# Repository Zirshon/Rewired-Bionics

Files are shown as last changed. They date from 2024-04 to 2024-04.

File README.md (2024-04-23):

In this file, there are instructions on how to recreate each part of Rewired Bionics' Waver Fin prosthetic attachment. Of these parts, the most likely to break is the body, and it is also the simplest to remake. It is recommended to save the spine if the body breaks and reuse that. If the Waver Fin breaks, it is not suggested to remake the shell. It is still fully functional without it, though it is more fragile without. The shell can be costly to remake, and requires specialized tools. If the spine breaks somehow, it is not suggested to personally remake it, as the tools required to make it can be dangerous  without prior training. Any further inquiries can be sent to loffenbe@asu.edu, jburdorf@asu.edu, or claypete45@gmail.com.

Manufacturing Process of Attachment:

  **In order to make a new body:** 
    To make a new body, PETG filament is required. The required tools are a 3D printer capable of printing the PETG filament with a printing area of at least 7"x7"x10" (A Prusa i3 MK3 was originally used), as well as a drill with a 1/2" bit.
    To make the new body, download the file labeled "Waver Fin Body.STL" and run it through a slicer. A slicer is a program designed to make STL files readable by 3D printers, and should be included with any 3D printer. They are all different and will likely require some researching on how to use them, but the details that should be used regardless are as follows: Use **100% infill**. This will prevent any water from being trapped in the body and molding. Print the Waver Fin **vertically**, such that the spine hole runs directly up and down. This is not technically required, but it will make the whole thing easier to clean up, and ensure it can survive the same forces it was tested for. Any sort of support material is fine, and should not affect the final stability of the Waver Fin, though tree support was what was used originally, and is generally fairly painless. Those are the only major settings to use, and it should be ready to print. The printing itself will take several hours. **Be sure to follow the temperature and printing instructions on the PETG filament**. 
    After it is done printing, remove the support material from it. This is usually as simple as snapping it off, though sometimes a decent amount of force is needed. Feel free to use pliers or any other sort of tools to speed it along. You may also want to use some sandpaper to get rid of risidual sharp edges from the supports. After you are satisfied, use the drill and bit to excavate the spine cavity of the body. 3D printers are never completely accurate, so this will likely be necessary. Make sure to keep the drill level while doing this, and stay on the path.
    The final step is now to put the spine back in the body. To do this, unscrew the adaptor. Place the body in a vice grip, tightening on the crossbar of the Waver Fin. Using a rubber mallet, gently hammer the spine down into the cavity until the top of the screw is level with the top of the body. Place a 2" washer with a 1/2" bore on the end of the fin, then rescrew an adaptor back on, torquing it into place.
    
  **In order to make a new shell:**
    To make a new shell, two sheets of kydex large enough to cover the body, as well as a new body and more filament is required. Also required is a vacuum former with the same dimensions as the kydex sheets (A Formech 686 was originally used), a 3D printer, and a heat gun.
    To make a new shell, first follow the directions to make a new body. Unscrew the adaptor and remove the washer. Download the two files labeled "Waver Fin Negative Left.STL" and "Waver Fin Negative Right.STL", then use a 3D printer to fabricate them, using 100% infill. PETG filament is recommended, but filaments like PLA or ASA could also work. Print flat on its back. No supports will be necessary. Using sandpaper, clean the finished Left Negative so that the body fits on it. Place the combined Left Negative and Body in the vacuum former, preferably with a grate on the bottom to allow for air flow. Following the directions on the kydex sheets, set the temperature settings on the vacuum former. Allow the vacuum former to preheat. Clamp the kydex into place, then begin heating it. It should be smooth, gummy and a little saggy, with a bit of bounce to it when it is ready to form. Following the vacuum former directions, form over the Waver Fin. It should be a fairly tight form. Allow it to cool a bit, but still remove the *negative* portion with some haste, **leaving the body in the shell**. Trim the excess kydex away once fully cooled, leaving some to fold over the body. Fold this over using a heat gun. Using sandpaper, clean the Right Negative until it can fit on the combined half shell and body. Once again place this in the vacuum former, and form over it, the same as before. Follow the same steps, removing the negative, trimming, and folding over. Try to get a tight seal. Remove enough material around the end of the fin so that the adaptor can screw on. Place the washer on and torque on the adaptor.
    
  **In order to make a new spine:**
    It is highly recommended to get this done by a metal shop, as a lathe is required and they are highly dangerous, even for trained craftsmen. The schematics for it are in the file labeled "Custom bolt shaft Drawing v2.pdf." Required for this is an aluminum bar 8.625" long with a 1/2" diameter. Also required is a socket cap screw with 3/8"-16 threads, and a length of 3/4", as well as some thread lock. 
    On one end of the bar, turn 1/2"-20 UNF-2A threads with a depth of 3/4". On the other end, bore out a hole with a depth of 3/4" and a diameter of 3/8", and turn 3/8"-16 UNC-1B threads on the inside of the hole. Screw the socket cap screw on, using thread lock.

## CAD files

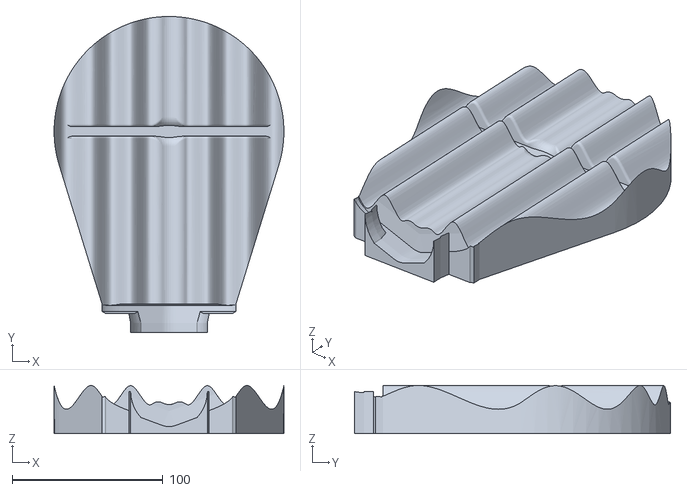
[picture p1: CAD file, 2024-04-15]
Waver Fin Negative Left.STL
152.4 x 209.6 x 31.9

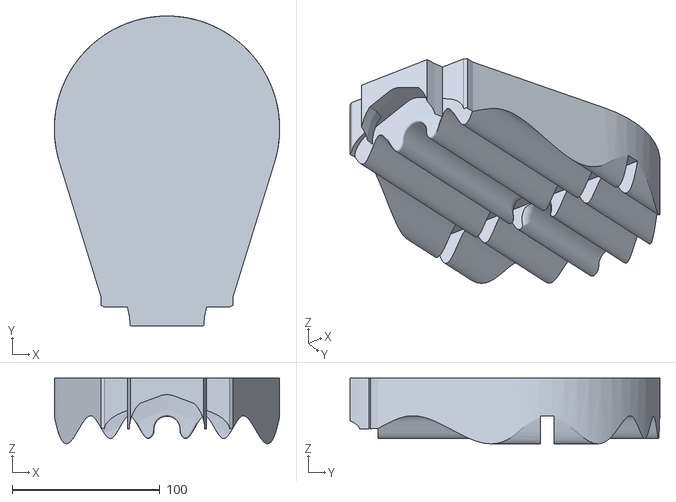
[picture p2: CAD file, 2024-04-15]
Waver Fin Negative Right.STL
152.3 x 209.5 x 44.3

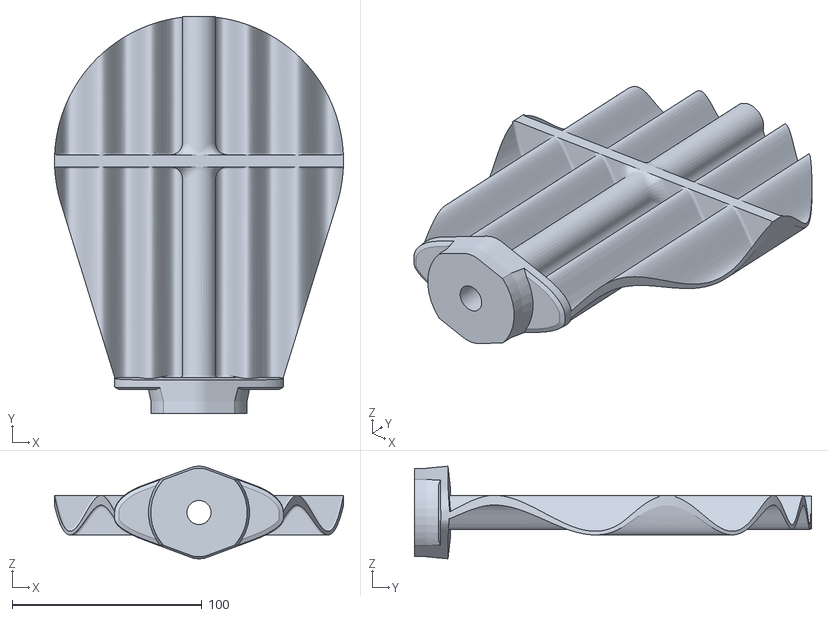
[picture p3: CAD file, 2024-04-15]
Waver Fin Body.STL
152.4 x 209.6 x 48.9

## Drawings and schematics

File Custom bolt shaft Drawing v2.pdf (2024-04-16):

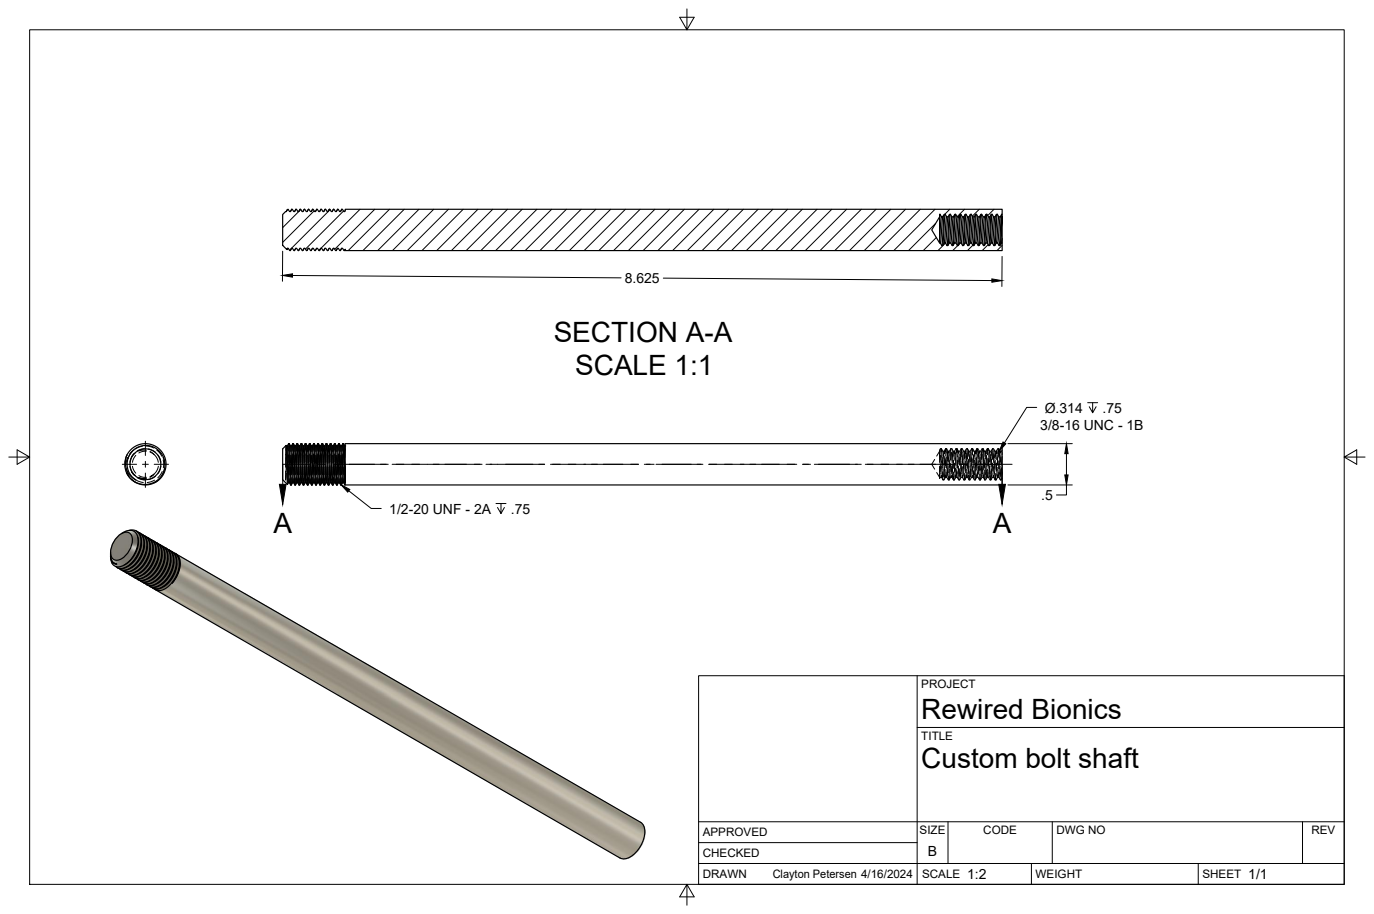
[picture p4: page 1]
SIZE; CODE; DWG NO; REV; Clayton Petersen 4/16/2024; SECTION A-A SCALE 1:1; 1/2-20 UNF - 2A; 3/8-16 UNC - 1B

PROJECT
Rewired Bionics
Custom bolt shaft
